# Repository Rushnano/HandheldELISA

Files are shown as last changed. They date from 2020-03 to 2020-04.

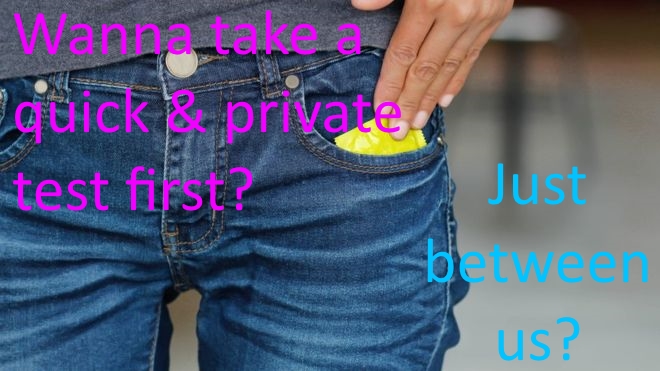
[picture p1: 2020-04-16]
images/wanna take a quick test first (annoted) 1.jpg

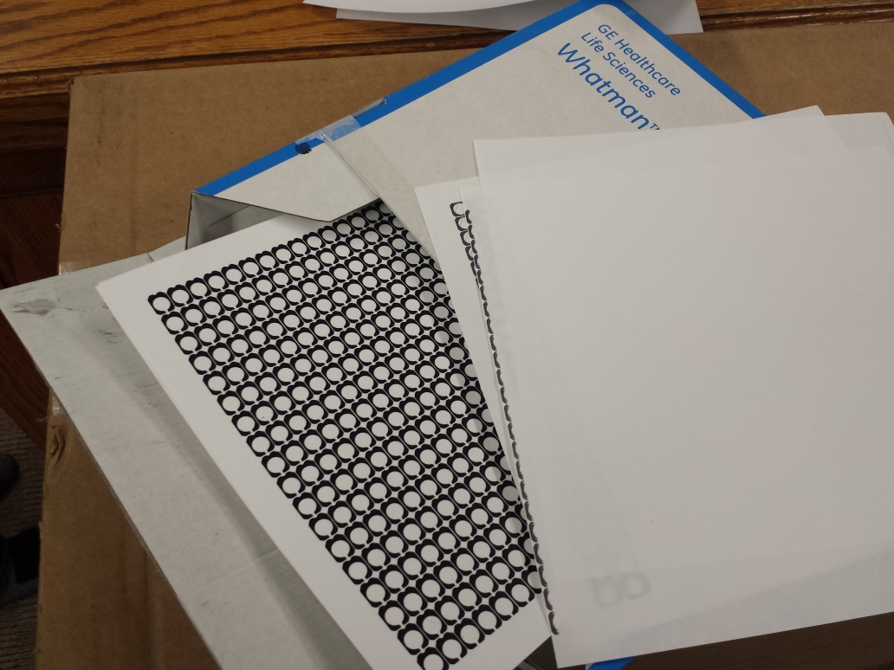
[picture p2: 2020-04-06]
screened electrode test sensors/Boundary printed 20200406.jpg

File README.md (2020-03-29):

# Handheld Point of Care ELISA
Electro Bio Chemical Potentiostat Testing Device for ELISA Test Cards
# 
  We are seeking contributors for creation of diversified testing device allowing consumable test cards capable of ELISA tests.

  The test cards may include protiens, enzymes, antibodies that allow capillary mixing and filtration with analyte so as to cause    a reaction in the working sensing zone. The working zone shall have excitation, sense and reference potentiostat electrodes for electronically sensing the the analyte/antibody reactions. The test card should also include near field radio frequency indentification for serial number, card test type, and date code.
  
  Added test card connections may also be included for electrophoresis as these electrodes may be required for fluidic movement. Hopefully we can limit these extra connections to the number of 8.

  The testing devices shall have circuitry and software included to perform a range of potentiostat test methods for a set of 2 electrode circuits. One set of electrodes will be sensing the real analyte response signal and the other set of electrodes will be used for relative reactions as reference. Potentiostat functions should be able to perform high resolution high sensitivity testing using static settings like many glucose meters to more complex features like differential pulse voltammetry.

  The testing device should be capable of near field radio frequency indentification reading for serial number, card test type, and date code to be used for test configuration parameters for that particular sensor card.

  App supported host connection using bluetooth should be included for intermediary cloud data services and display.

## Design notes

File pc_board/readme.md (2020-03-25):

#PC Board design notes

For now we will be using Altium for the source file application.

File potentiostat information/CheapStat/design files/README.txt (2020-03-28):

from: https://web.chem.ucsb.edu/~kwp/cheapstat/

schematic/ contains the EagleCAD files for schematic and board layout, parts list, and Gerber files for PCB manufacturing.

gui/ contains the Java program for receiving results from the CheapStat device via USB.  Source code is located inside .jar file.

mcu/ contains the firmware for the MCU as well as the source files.  AVRstudio 4 and WinAVR are required for compiling source code, and well as AVRISP mkII or equivalent programmer for programming the MCU.

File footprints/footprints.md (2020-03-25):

This is where the pc board part footprints will be located.

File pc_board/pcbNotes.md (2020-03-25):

PC Board design notes

For now we will be using Altium for the source file application however gerbers, pdf or image files may also be used for collaboration efforts.

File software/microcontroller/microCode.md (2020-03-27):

This is where low level firmware code will be stored primarilly in ansi C / C++. some assemble may be required. :)

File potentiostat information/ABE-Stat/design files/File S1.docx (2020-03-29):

# BE 350L

# Lab 3A Handout - Stepper Motor Control

# AEI 123 October 19, 2017

AEI 123 October 26, 2017

Report Due November 9, 2017

Revision Due November 23, 2017

In this lab exercise, you will use your Arduino skills to develop the code to control the speed of a stepper motor. Your code will issue commands to a stepper motor controller circuit “Big Stepper Driver”, via controlled pulses from a digital I/O port on the Redboard. The controller will interpret those timed pulses and sequence current to the individual motor windings accordingly. Stepper motors (a class of “brushless DC” motors that are commutated electronically by energizing individual coils in the stator, in contrast to traditional DC motors which alternate the current through brush contacts as the rotor turns) are commonly used in motion control applications because the position can be easily controlled down to the resolution of a single (or even a half) “step” without the use of sensory feedback. The motor you will use in lab (Mercury motor - spec sheet attached) is a 12V (nominal) two-phase bipolar stepper motor with 200 steps per revolution of the rotor.

You will be provided a sketch with the code for the user interface (menu) that prompts the user to select for the following options.

1. Move forward a fixed number of steps upon button press.
2. Move backward a fixed number of steps upon button press.
3. Pipette mode. Uptake media upon first button press. Dispense upon second button press.

For the first part of the lab exercise, we will create an algorithm for a controlled acceleration to the specified speed, continue at the specified speed until within 50 steps of the total steps, and then slow the speed to zero when the total number of steps have been traveled. The mechanism for turning the motor by a single step is to create a square wave pulse by turning a digital port on and then off. The motor speed will be dependent on the frequency of the pulses, so part of your algorithm will be to determine the appropriate delay between each pulse.

For example, a speed of 500 steps/sec is accomplished by pulsing the digital port HIGH for 1 ms then low for 1 ms for a total of 2 ms per step. This is the close to the maximum speed with this hardware configuration (0.7 ms delay). Similarly a speed of 1 steps/sec is accomplished by pulsing the digital port HIGH for 500 ms then low for 500 ms for a total of 1000 ms per step.

1. Open the provided stepper motor sketch “Steps test”. An external library will not be required for this application.
2. Write the code for the Steps function. The Steps function should move the motor through the specific number of steps from the revolutions setting. This function will calculate the required delay and turn the digital output port HIGH and then LOW for each step required for motion.
3. Test your code by observing the motor rotate in both directions through several angles of shaft rotation.
4. Open the provided stepper motor sketch “Lab 3 Start”. Insert the Steps function into the main loop to implement the menu functions.
  a. Move counter clockwise a fixed number of steps upon button press.
    i. Set direction.
    ii. Implement Steps function.
    iii. Reset ACTIVATE status.
  b. Move backward a fixed number of steps upon button press.
    i. Set direction.
    ii. Implement Steps function.
    iii. Reset ACTIVATE status
  c. Pipette mode (part 1). Sample upon first button press.
    i. Set direction.
    ii. Implement Steps function.
    iii. Reset ACTIVATE status
  d. Pipette mode (part 2). Dispense upon second button press.
    i. Set direction.
    ii. Implement Steps function.
    iii. Reset ACTIVATE status
5. Upload the sketch to the Redboard.
6. Power down the Redboard.
7. Connect the Redboard to the stepper motor controller.

Redboard | Controller Input
2 3 4 5 6 7 GND VCC | STEP DIR MS1 MS2 MS3 EN GND 5V

8. Make sure that the Stepper motor is connected correctly to the controller. The motor is a 12 VDC nominal bipolar stepper motor with 200 steps/ revolution. The motor leads are connected to the controller as below.

Motor | Controller Output
Red | A1
Green | A2
Yellow | B1
Blue | B2

9. Connect the drive power leads to an isolated power supply at 12 VDC (M+, GND). Do not turn on power supply.
10. Check all connections before turning devices on. Turn on Redboard first and then power supply.
11. Test your code with the 360° scale and a stop watch for forward and backward movement. Also make sure all menu functions work.

Figure 1. Sample square wave signal to control the speed of a stepper motor with the “Big Easy Driver” controller.
BE 350L

Lab 3B Handout – Automated Pippetor

For this lab you will be testing the ability of an automated pipetter to dispense liquid in both accurate and repeatable volumes. You will use the pipette driver program to run your motor controller subprogram.

1. The dispensing cycle is described in the table below. As before, the system should wait for your manual confirmation before taking a sample and dispensing a sample.

Action | Algorithm

Manual Confirmation
Take Sample | 1. Raise plunger from initial position to some top position.

Manual Confirmation
Dispense Sample | 2. Lower plunger from top position to initial position
| 3. Lower plunger from initial position to purge position.
| 4. Raise plunger from purge position to initial position.

1. Develop an experimental procedure to adequately test the ability of the pipette apparatus to dispense water. Use your experience from previous lab exercises to generate a series of tests where the travel of the plunger is compared to the volume of water dispensed and calibrate the device. Evaluate the calibration by performing additional tests while controlling the motor to dispense calibrated volumes rather than displacement settings.
2. Ensure the data set is adequate in both range and repetition to analyze the accuracy and repeatability of the pipette.
3. You will be able to measure the mass of water dispensed with an analytical balance.
4. **Prevent the motor from driving the plunger too deep and hitting the bottom of the syringe tube.

BE 350L, Fall 2017, Lab 3 Handout 1

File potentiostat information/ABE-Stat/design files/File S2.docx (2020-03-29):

BE 350L
Final Design Project
Report Due December 7, 2017

Design of thermal cycling unit for DNA amplification through polymerase chain reaction (PCR).

This lab exercise will involve the design of hardware and software components of a temperature control system. The intended application is a thermal cycler to enable the different steps required for polymerase chain reaction (PCR) amplification step. In PCR, double stranded DNA is “melted” apart at high temperature, then annealed to single stranded “primer” DNA at a lower temperature, that initiates extension of complementary sequence onto the original template DNA at an intermediate temperature. Copies of the original template DNA are then made for each thermal cycle. We will focus on temperature control for one of these steps, the actual the amplification process which can be accomplished at ~50 °C.

Thermocouples/Peltier Cooling Effect

Thermocyclers typically use Peltier cooling units to control the DNA sample temperature. The scientific principle behind the Peltier cooling technology is similar to that of a thermocouple. In a Peltier cooler, an electrical potential is applied across the junctions of two dissimilar metals, resulting in transfer of thermal energy from one junction to the other (i.e. one junction is heated while the other is cooled). Changing the polarity will reverse the direction of heat transfer, allowing one junction to be alternatively heated or cooled. In a typical Peltier unit, there are many small junction points and this arrangement is called a thermopile. Some complicated temperature measurement devices such as calorimeters also use thermopiles as a complex network of thermocouples to measure temperature around a sample in all three dimensions.

Peltier coolers are solid-state devices without any moving parts. The advantages include size, material cost, ability to cool below ambient temperatures, reliability, and low maintenance requirements. The disadvantage is that the cooling is not energy efficient and that heat from the hot side of the cooler must be constantly dissipated during operation. One of the main things to remember about a Peltier unit is that voltage only corresponds to a thermal energy difference between the two sides rather than a desired temperature at a particular side. Therefore if cooling is desired, then heat must be dissipated from the hot side so that the specified cold temperature is maintained. Alternatively, if heating is desired, heat must be directed to the cold side so that the specified hot temperature is maintained. While the rate of thermal energy transfer is proportional to the applied current between the junctions, application of current also results in ohmic heating throughout the device which is proportional to the square of current. Therefore there is a physical limit to how much a junction can be cooled even if the “hot” junction is maintained at ambient temperature.

State 1

Temperatures of each side are the same T1 = T2.

TC

State 3

Side 1 cooled. Heat pumped from cold side to hot side. Lowest TC achieved by ΔT = TH - TC. Must remove heat from hot side keep TH from rising too high.

TH

TH

State 2

Side 1 Heated. Heat pumped from cold side to hot side. Highest TH achieved by ΔT = TH - TC. Must draw in heat to cold side keep TC from falling too low.

TC

T1

T2

Figure 1. Illustration of temperature control for cooling and heating applications with a Peltier cooler.

The rate at which the Peltier unit can pump heat from its cold side to hot side is a function of the temperature difference between the two sides. The measured performance as supplied by the manufacturer Cui Inc. is given in Figure 2. At a given voltage applied to the terminals, e.g. 4 V, the top plot can be used to determine current draw. That current draw can then be located on the bottom plot to determine a relationship between the heat pumped and the temperature difference between the two sides.

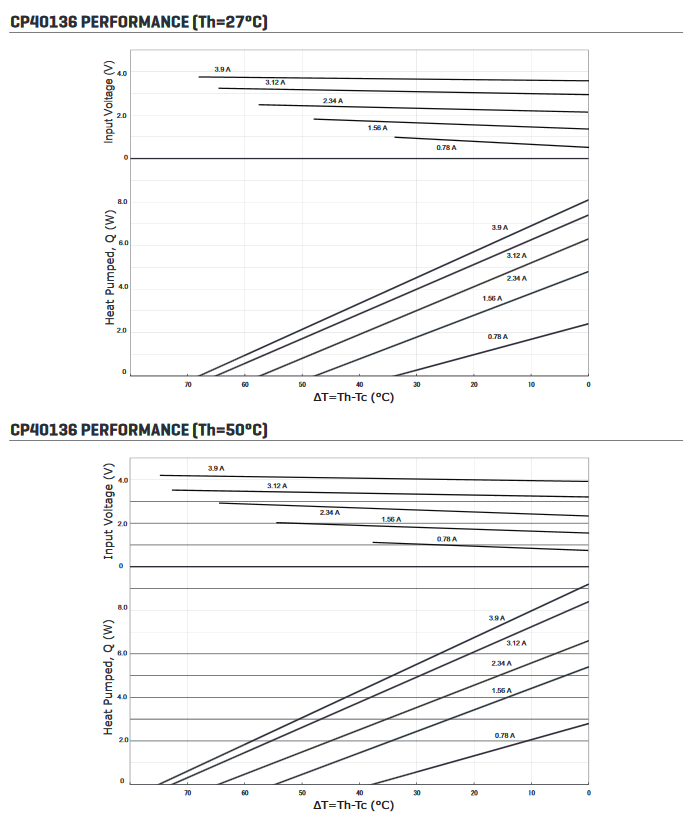
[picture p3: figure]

Figure 2. Performance of the CP40236 Peltier cooler at hot side temperatures of 27 and 50 °C.

Methods

The performance criteria that you will be evaluating are 1) rate of temperature change within the sample as well as 2) a uniform temperature distribution within the sample. You must design the heat sink such that you obtain a reasonable temperature ramping. You must also consider how to achieve a uniform temperature distribution within the sample.

Over the course of this multi-part laboratory exercise, there are several exercises to be completed. Remember, these are methods and the actual experimental objective(s) should be written in your own words.

- First generate an analytical model on this thermocycler system. These first calculations will serve as the basis for future decisions with the heat sink design and analysis of the results. Run models for both heating and cooling processes by changing the initial temperatures.
- Conduct simulations within Solidworks to further study not only the temperature ramping, but also the temperature distribution within the sample. Again, run models for both heating and cooling processes by changing the initial temperatures. Submit a final heat sink design for fabrication by the instructor.
- Design and conduct experiments on the thermocycler using the heat sink that the group has designed.
- Analysis will be made on all of the above results and design changes should be proposed if necessary.

Analytical Model

During the first period you will be performing basic energy balance analyses to characterize the temperature change over time for a sample block and heat sink fabricated from 6061 aluminum. The dimensions of the sample block and initial heat sink are 1” x 1” x 0.75” and 3” x 1” x 0.5” respectively. You may assume that heat conduction within the aluminum occurs much faster than all other processes such that the temperatures are uniform within the sample block and heat sink separately. Initially you may choose a constant power transfer between the two blocks, however you should refine your model to include a formula for the power transfer derived from the manufacturer’s data table for your Peltier unit. Assume that the sample block and heat sink exchange heat with the ambient air, but do not exchange heat with each other. This model will help determine the power transfer value to use in the computer simulation. You will need to look up an appropriate convective heat transfer coefficient for air. You may (should) use Matlab to execute the solution of this non homogeneous system and to plot your results.

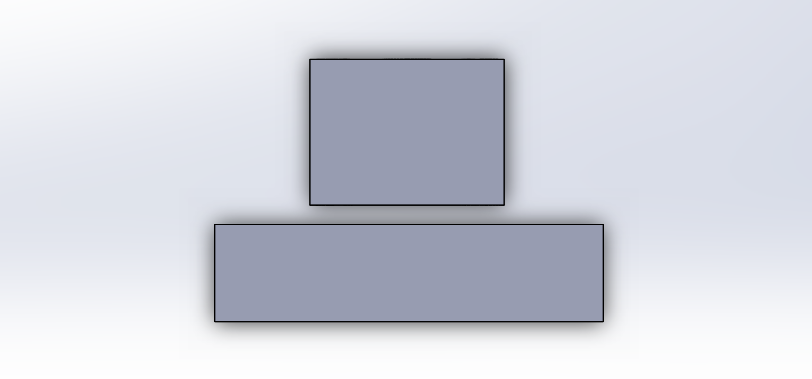
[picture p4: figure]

Figure 3. Layout of the sample block (above) and heat sink (below) in the thermocycler. Peltier unit not pictured.

Heat Sink Design

Alter the design of the heat sink either by changing the size or by adding fins or other geometries to enhance convective heat exchange. Design the heat sink to maintain temperatures that are desirable for the heating and cooling cycles of the thermocycler. Strike a balance between increasing the surface area while preserving the mass of the heat sink. The minimum and maximum dimensions for the heat sink are 1” x 1” x 0.5” and 1” x 3” x 0.5” respectively. Each participant should design at least one of their own heat sinks.

Solidworks Simulation

During the second period, you will be using Solidworks to create 3D drawings for the heat sink, sample block, and DNA (water) sample separately. Complete these drawing using the provided specifications. Solidworks will then be used to run multiple thermal simulations. Just as with your initial analyses of this system, you will need to define any process that will affect the energy stored in each component as well as the initial conditions, material properties, and boundaries. Solidworks will divide the parts into a finite number of elements and calculate the heat transferred between adjacent elements. This technique is called finite element analysis.

The simulation for the sample block and heat sink will be conducted separately. For the sample block simulation, insert the sample block and sample parts into an assembly and add the appropriate mating constraints to align the parts. This can be reviewed together in class.

1. Open a New Study under the Study Advisor drop down menu in the Simulation tab. Select a Thermal study for the current simulation. Take note of the parameters of the thermal study as seen under the Feature Manager window on the left.
- Parts – Select material composition of each part.
- Connections – Choose whether contacts between components will be insulated.
- Thermal loads – Processes that affect the energy stored in each component
  - Temperature – Can set an initial temperature of component or define a constant temperature to a surface.
  - Convection – Define a convective heat transfer process.
  - Heat Flux – Define a constant heat transfer flux process (power/area).
  - Heat Power – Define a constant heat transfer process.
  - Radiation – Define a radiative heat transfer process.
- Mesh – Create parameters to generate the finite element mesh.
2. Right click on the name of the study and choose to edit Properties. Change the study from a steady-state to a transient analysis and set the time range and time step.
3. Add/Edit the material for each part and select 6061-T6 aluminum for the sample block and heat sink. Select water for the sample.
4. Create an Insulated contact set.
5. Add a Temperature thermal load. Select Initial Temperature and select both components. Set the temperature to 25 °C. This thermal load must be the first one added.
6. Add a Convection thermal load. Look up an appropriate convective heat transfer coefficient and select an ambient temperature of 25 °C.
7. Add a Heat Power thermal load. Select the top face of the heat sink and define the heat power.
8. Add a Heat Power thermal load. Select the bottom face of the sample block and define the heat power.
9. Create a Mesh and then Run the simulation.
10. You can save a copy of the resulting surface plot as a jpeg file.
11. Create a Section Clipping to display the internal temperature uniformity of a slice.
12. Under Plot Tools, use the Probe option to select points along the cross-sectional slice and choose a Response plot to display how the temperature changes at specific points over time.

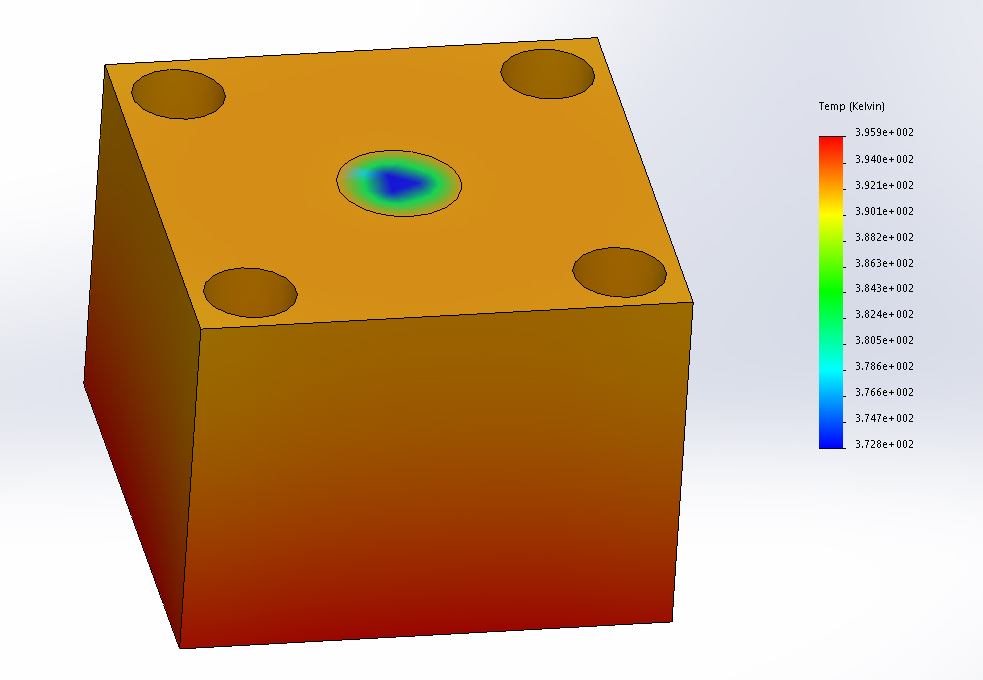
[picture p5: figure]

Figure 4. Color plot of the temperature distribution along the surface of an aluminum sample well block with heating along the bottom surface. Note that due to the relatively high thermal conductivity of aluminum the temperature distribution is mostly uniform.

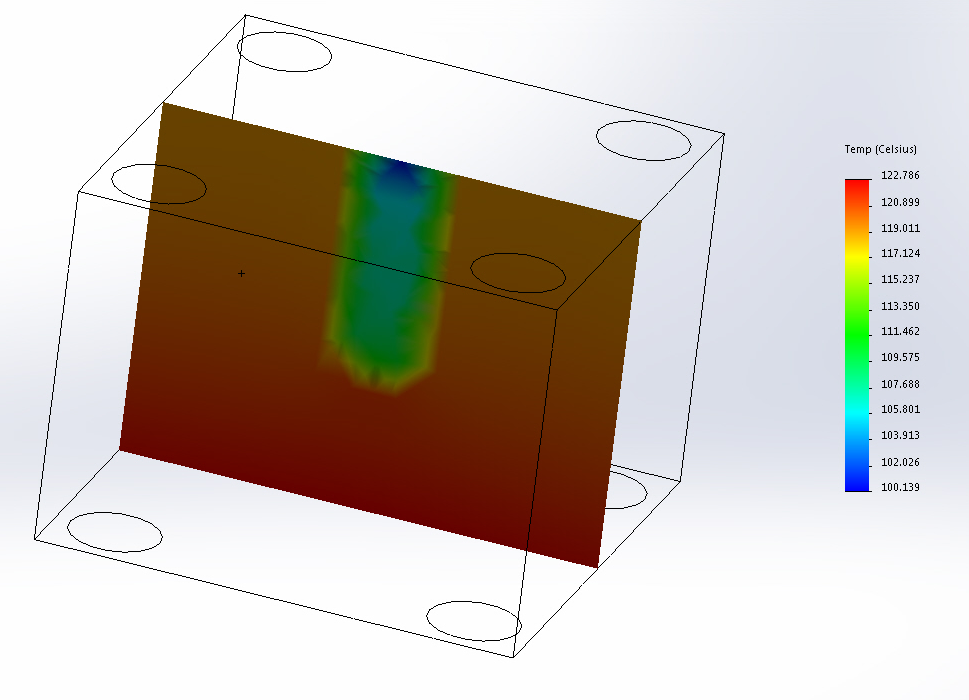
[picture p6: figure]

Figure 5. Temperature distribution of a cross section through the center of the middle reaction well. Notice that the bottom and sides of the well are hotter than along the top and center.

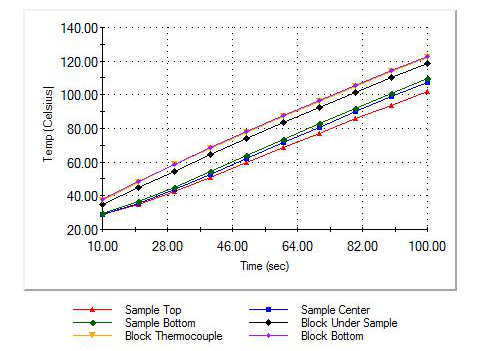
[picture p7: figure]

Figure 6. Transient temperatures simulated at multiple points along the sample well axis. Note that the bottom of the well responds faster and gets hotter than the top.

13. Right click on the thermal study tab and duplicate the study. You may choose to name the new study “cooling” or something similar. Modify the study to simulate cooling of the sample block and water sample assembly. Change the initial temperature to 50 °C and the reverse the direction of the heat power. Run the simulation again and save any desired results in tables or graphs.
14. Run cooling and heating simulations for the heat sink which you can conduct right from the part file. You do not need to create an assembly. Save any desired results. Each group member can run simulations with the heat sink they designed.
15. At this stage, you can also redesign your heat sink within the model window. Modify the heat sink by changing the length or cutting away material. Before you run new cooling and heating simulations, apply a mesh again. This will update the geometries in the thermal studies and you should not need to redefine all the parameters again.

Experimental Procedure

16. Design and conduct experiments to validate your simulation results. Make notes of any assumptions made during the simulation and design your experiment to be as consistent with most of these assumptions as possible. Each test that you run, may help you to not only assess the design but also refine your simulation settings, for example the convective heat transfer coefficient value or power addition/removal.

Minimum Report Requirements

17. The report should have the usual required sections.
18. Recall the two design criteria. There should be a timely temperature ramping to the desired temperature and the temperature of the sample should be relatively uniform.
19. There will be a lot of information that can go in the methods section and you will need to organize it and present it well. From the analytical model, you will get an idea for what the heat transfer power range of the Peltier unit will be as well as model for the temperature of the components as a function of time. This information along with your research into an appropriate convective heat transfer coefficient value will likely have a significant impact on the simulation results. How you determined these parameters should be explained in this section.
20. There can also be an abundance of graphs and results for your results and discussion section, so again organize and present the material well. Simulation and experimental results should be discussed here individually as especially as relating to the objectives as well as compared. After analyzing both results, you modified the simulation, discuss that here as well.
21. In the conclusion, briefly summarize the results in the context of the objectives. Also suggest design changes or the next step(s) in the design or development process.

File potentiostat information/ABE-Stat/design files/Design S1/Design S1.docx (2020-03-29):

Supplemental Material, Design S1 (Coffee Cherry Color Sorter)

Schematic

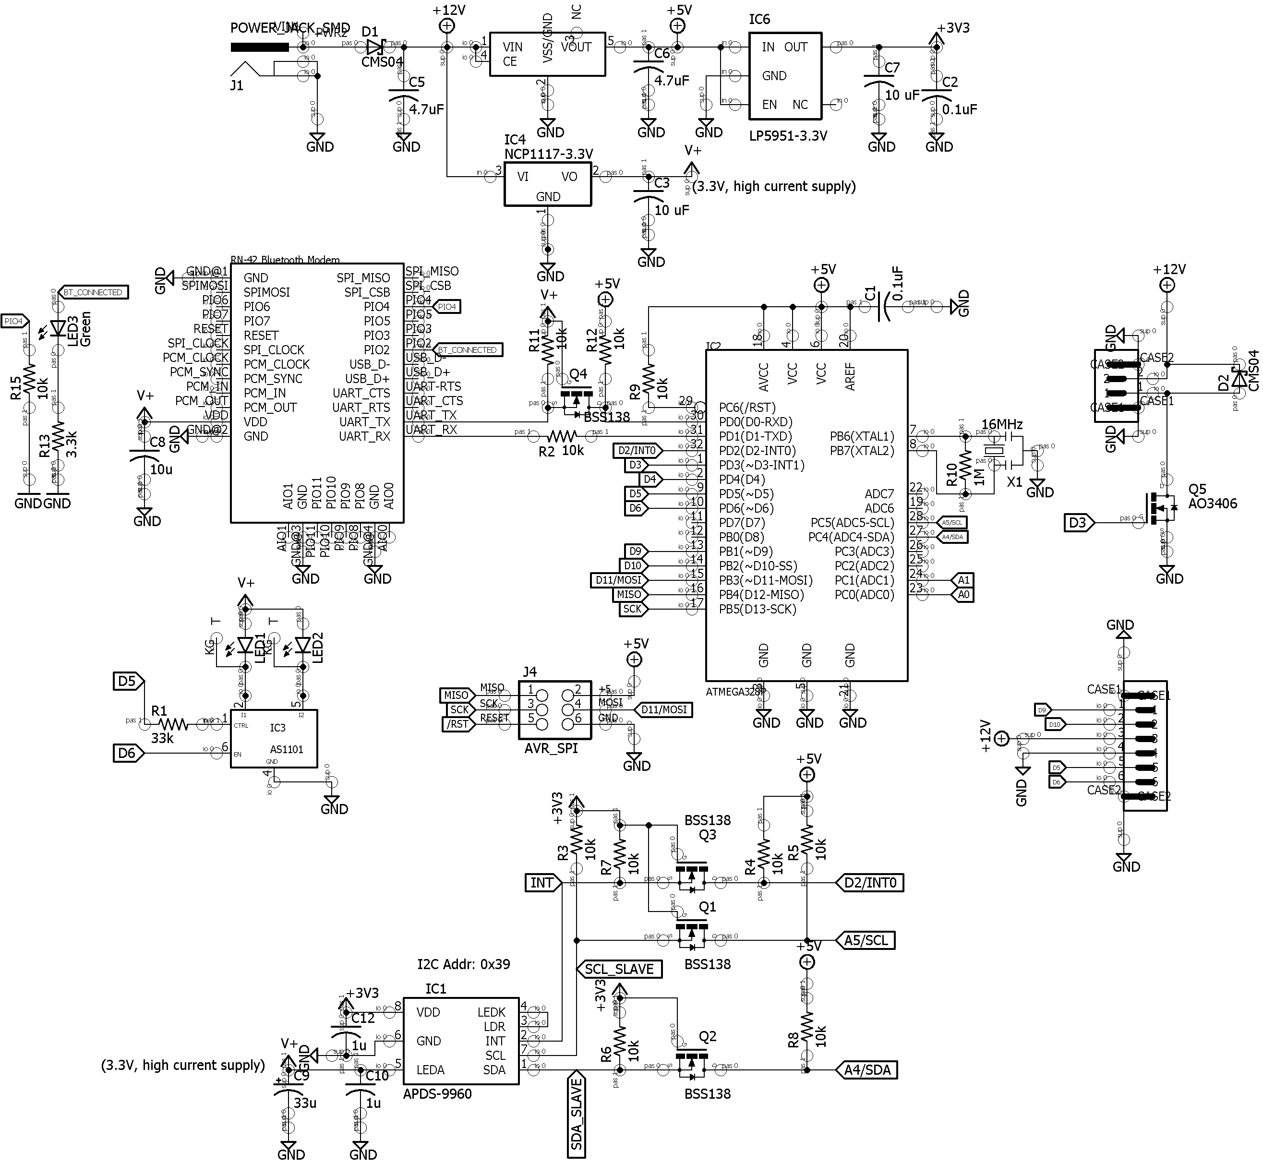
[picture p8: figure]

Layout

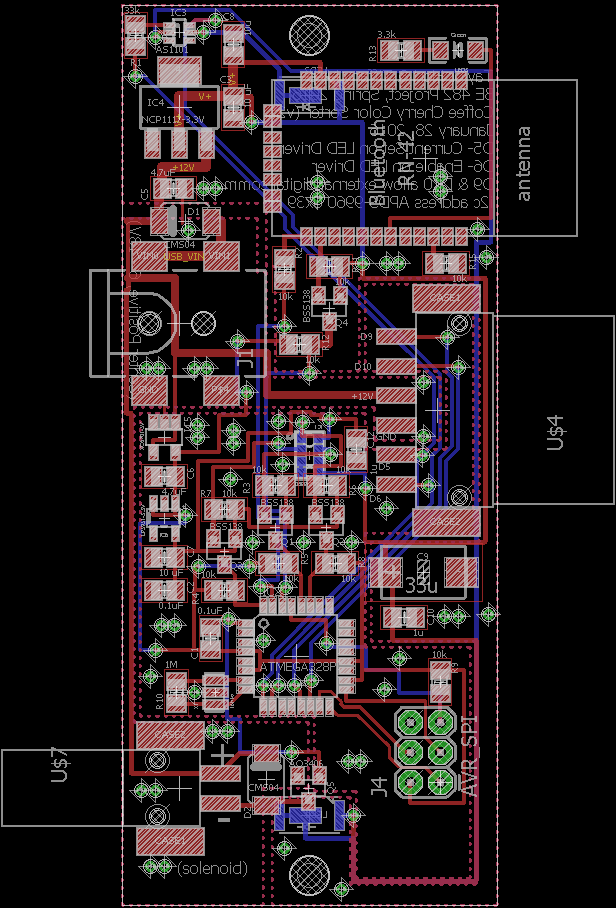
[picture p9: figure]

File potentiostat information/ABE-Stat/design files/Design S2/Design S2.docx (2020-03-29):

Supplemental Material, Design S2 (ABE-Stat 1_0_01 Wireless Potentiostat Prototype)

Schematic

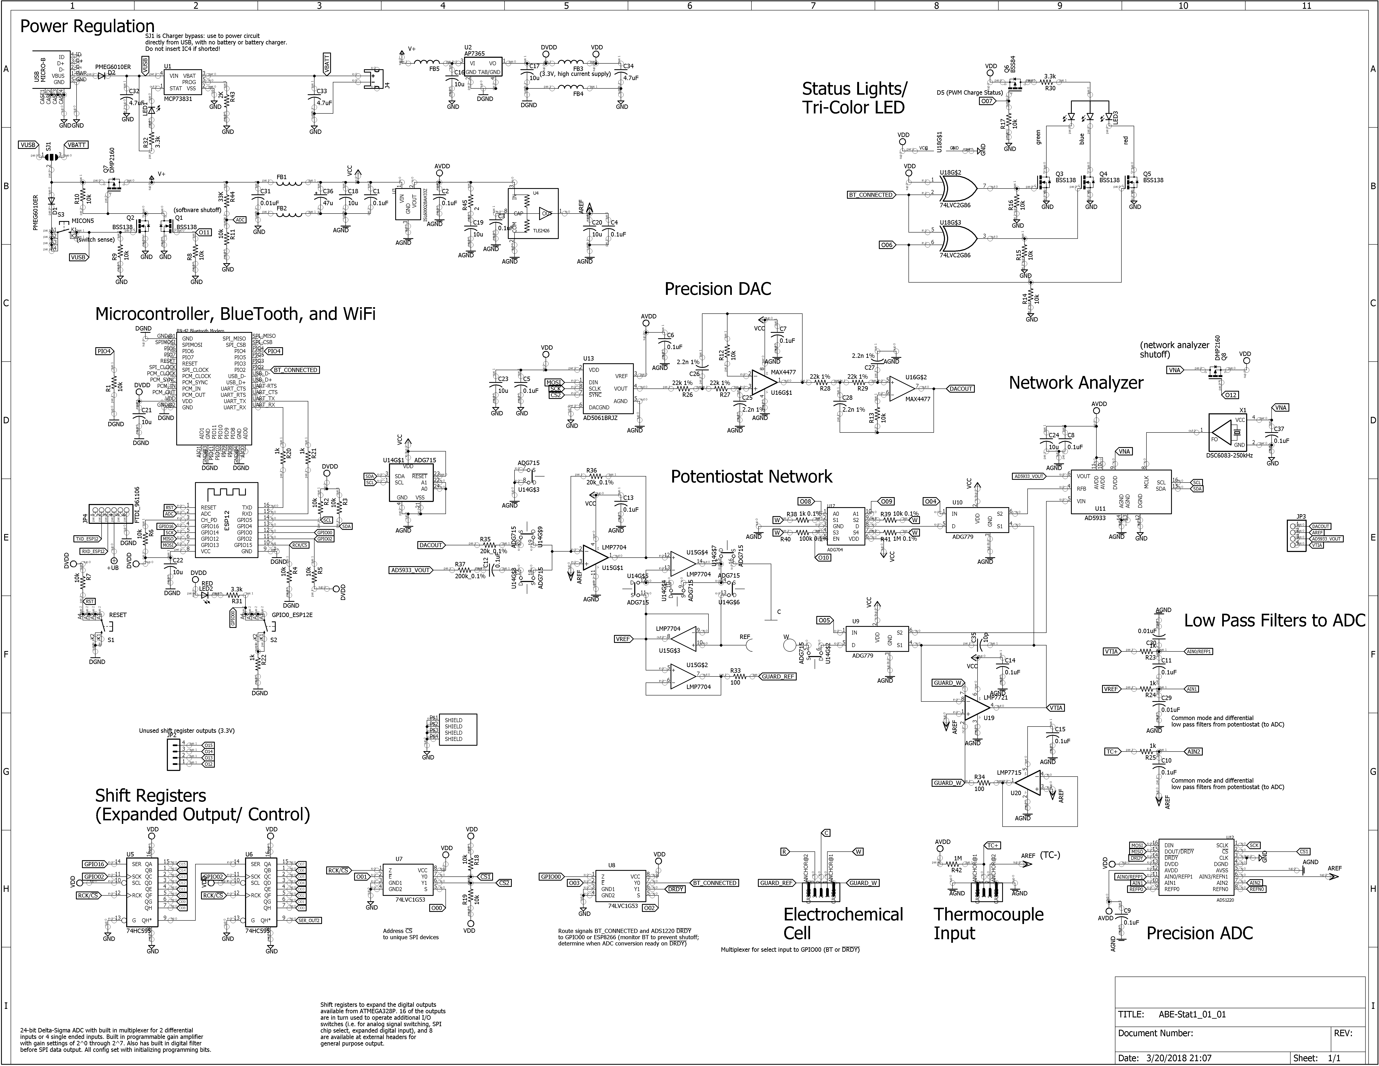
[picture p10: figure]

Layout

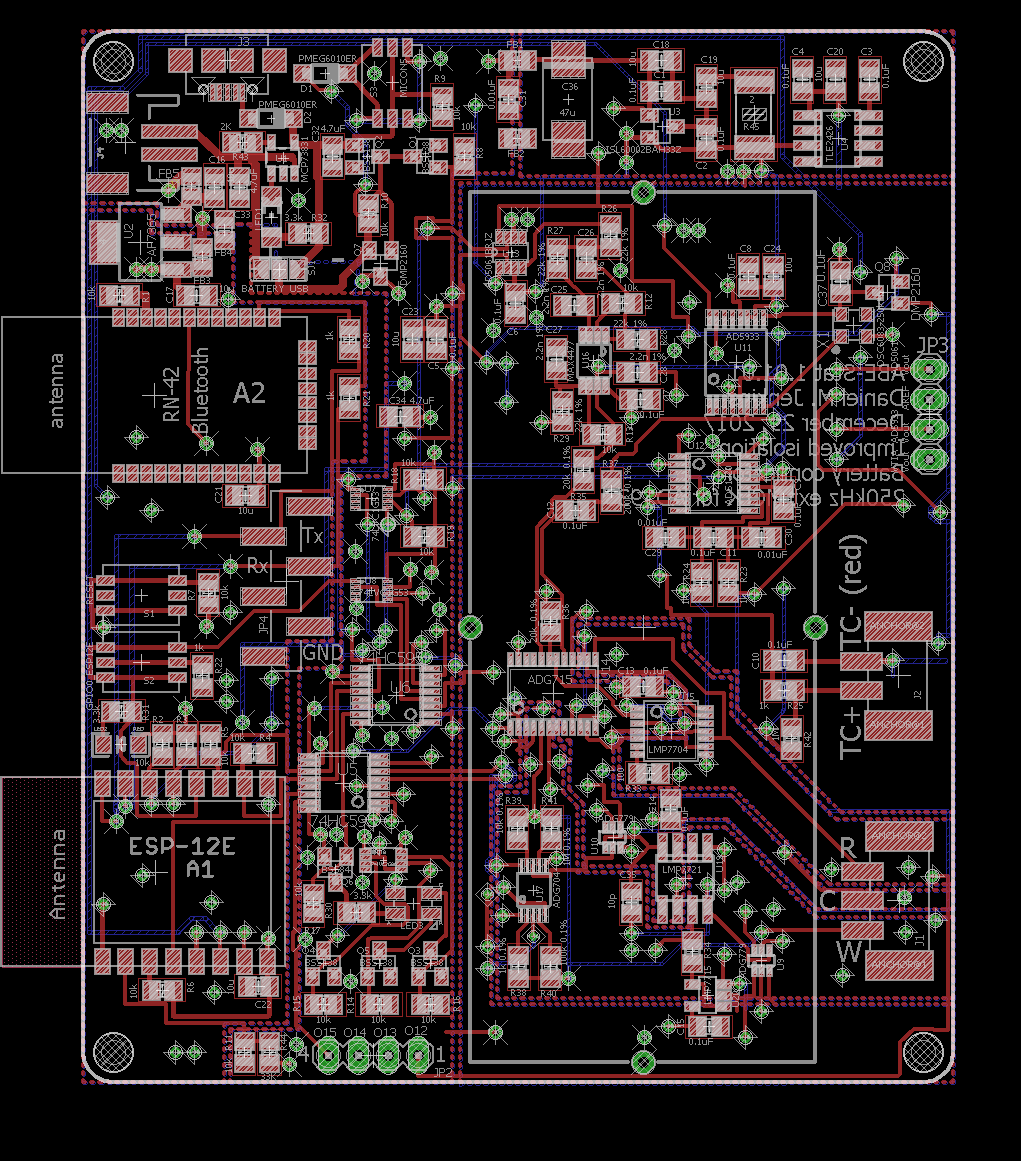
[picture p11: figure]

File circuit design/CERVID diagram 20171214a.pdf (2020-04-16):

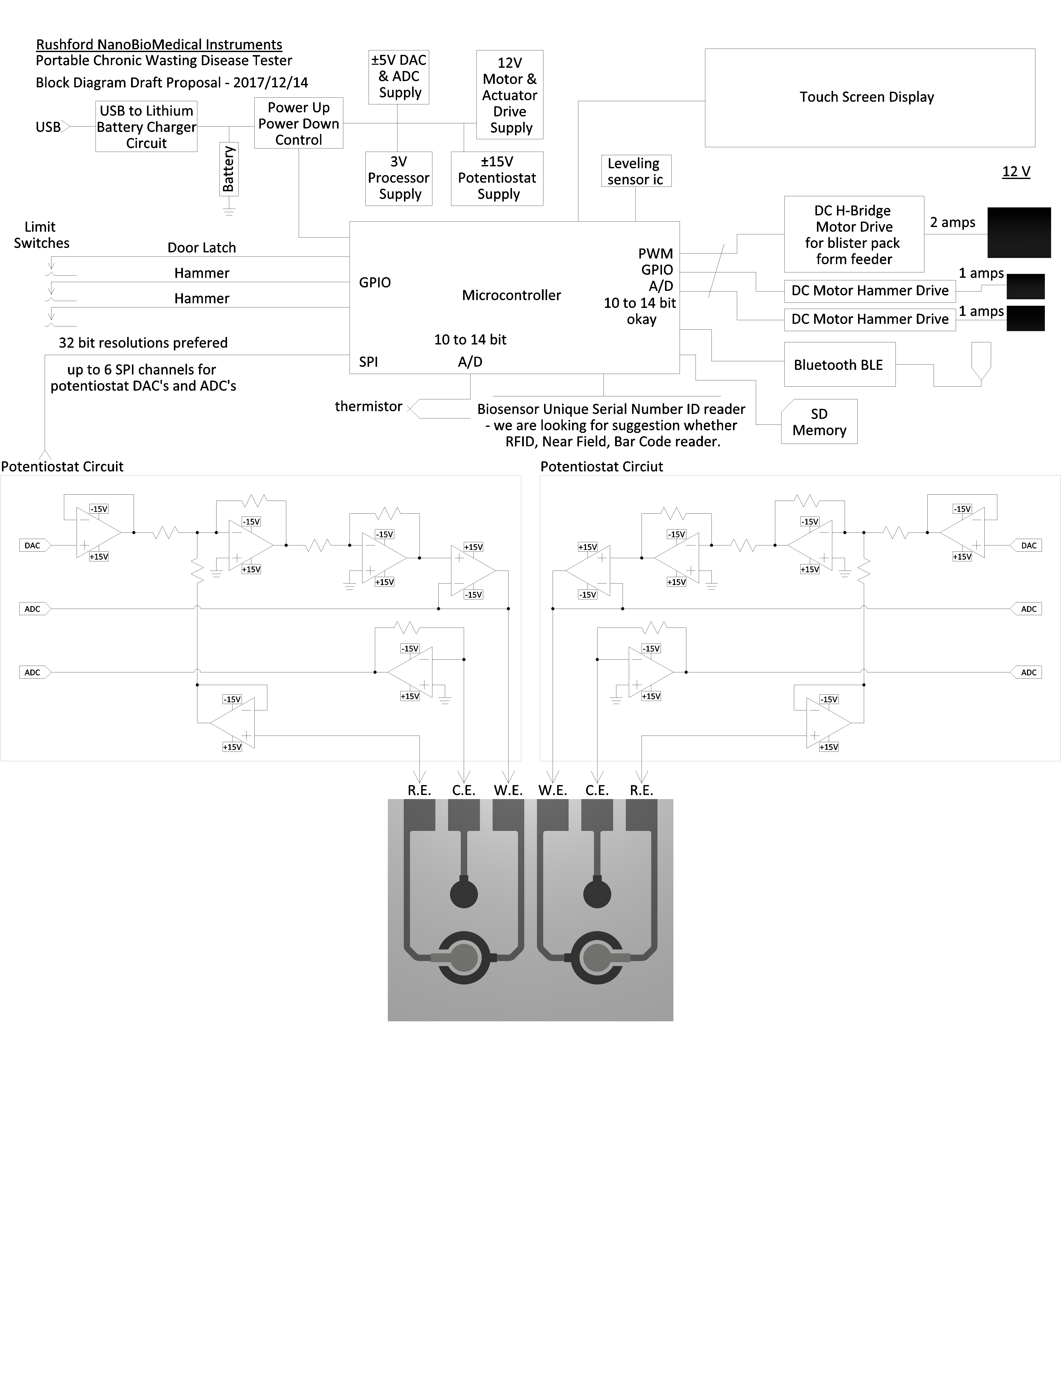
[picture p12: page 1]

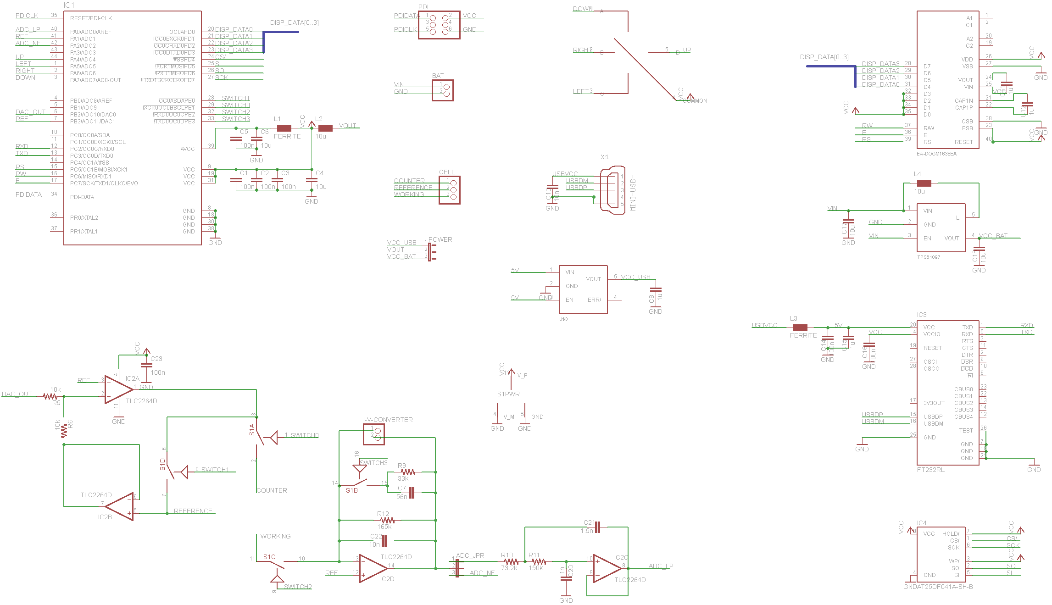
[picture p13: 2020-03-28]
potentiostat information/CheapStat/design files/schematic/schematic.png

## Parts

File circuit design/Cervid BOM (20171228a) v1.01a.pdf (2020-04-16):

Cervid BOM v1.01a.xls

Line Item | Quantity | Reference Designation | Value | Description | Manufacturer | Part Number
1 | 1 | U1 | | Microcontroller | Texas Instruments | MSP430F5529IPN
2 | 1 | U2 | | Bluetooth LE Controller | Texas Instruments | CC2640R2FRHBR
3 | 1 | U3 | | 32 Bit Digital to Analog Converter 2 Channel | Asahi Kasei Microdevices | AK4493EQ
4 | 1 | U4 | | 32 Bit Analog to Digital Converter 4 Channel | Asahi Kasei Microdevices | AK5534VN
5 | 1 | U5 | 8-38V 2.8A | Motor Driver - Form Feed | Texas Instruments | DRV8801RTYR
6 | 1 | U6 | 4-18V 1.4A | Dual Solenoid Drivers - Bladder Hammers | Texas Instruments | DRV8846RGER
8 | 1 | U7 | 3.3V | Switching Power Supply 3.3V | Texas Instruments | TPS61221DCKR
9 | 1 | U8 | 5V | Switching Power Supply 5V | Texas Instruments | TPS61222DCKR
10 | 1 | U9 | 12V, 2A | Switching Power Supply 12V | Linear Technology | LT1109ACS8-12#PBF
11 | 1 | U10 | ±15V | Switching Power Supply ±15V | Texas Instruments | TPS65130RGER
12 | 1 | U11 | | Angle Sensor | NXP | KMZ49,118
13 | 7 | U12, U13, U14, U15, U17, U18, U19 | | High Impedence, High Slew Rate, Low Noise Op Amps | Texas Instruments | OPA637AU
14 | 1 | Y1 | 32.768kHz | Crystal | Seiko | SSP-T7-F
15 | 1 | H1 | | Secure Digital Memory Socket | Amphenol | 101-00405-75
16 | 1 | H2 | | Mini USB Connector | Amphenol | 10118194-0001LF
17 | 1 | H3 | | Litium Battery Connector | JST | S2B-PH-K-S(LF)(SN)
18 | 1 | H4 | | Display Connector | TE Connectivity | 84952-6
19 | 1 | DISPLAY | | Touch Screen Display | Displaytech | DT035BTFT-PTS1

Resistors
Capacitors
Inductors
Connectors
Limit Switches

NFC/RFID Biosensor ID

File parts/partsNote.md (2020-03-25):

Evaluated and implimented technical part documents will be located here.

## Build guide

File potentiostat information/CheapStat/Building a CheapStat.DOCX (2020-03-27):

General Instructions for building a CheapStat portable potentiostat.

1// Circuit Board

Send the Gerber files to a printed circuit board manufacturer, and order one or more of the CheapStat printed circuit boards. The gerber files are available as supporting information, and updated versions may be found on our website.

2// Parts List

Order the parts from a vendor such as digikey or Mouser electronics. See table S1 for a full list of parts. Some of these components may be substituted or omitted. For instance, this device can function with a wide variety of different flash chips.

3// Soldering

Solder all of the components onto the printed circuit board as indicated in figure S1. You can zoom in on this schematic, or look at the gerber files and the photos below (S2 and S3) for further clarification. If you do not have the appropraite soldering equipment, contract circuit assembly firms such as Sandberg Industries (Santa Ana, California) can do it for you for a reasonable fee. Be sure to wear an antistatic wrist strap when handling the components.

4// Mounting the board.

You will need to cut several holes in the enclosure (Fig S2 and S7) to handle the LCD display, USB port, and control switch. This can be done with a dremmel rotary tool.

5// Programming the microcontroller.

On the circuit board, there are a set of six pins that can be plugged into a microcontroller programmer. First, attach the cheapstat to a USB power source. Then, attach the microcontroller programmer. Finally, upload the firmware files to the microcontroller (available in supporting information). This process should take a few minutes. This is the final step of the assembly process.

6// Using the cheapstat

With the CheapStat plugged into the USB port of a computer, start the control software program. Use the four way switch on the CheapStat to select an experiment mode such as Square Wave Voltammetry, change the parameters, and run an experiment. Be sure that the control software is set to the correct COM port.

7// Handling Data

Data from the cheapstat can be copied directly into Microsoft Excel, Open Office, or other spreadsheet programs.

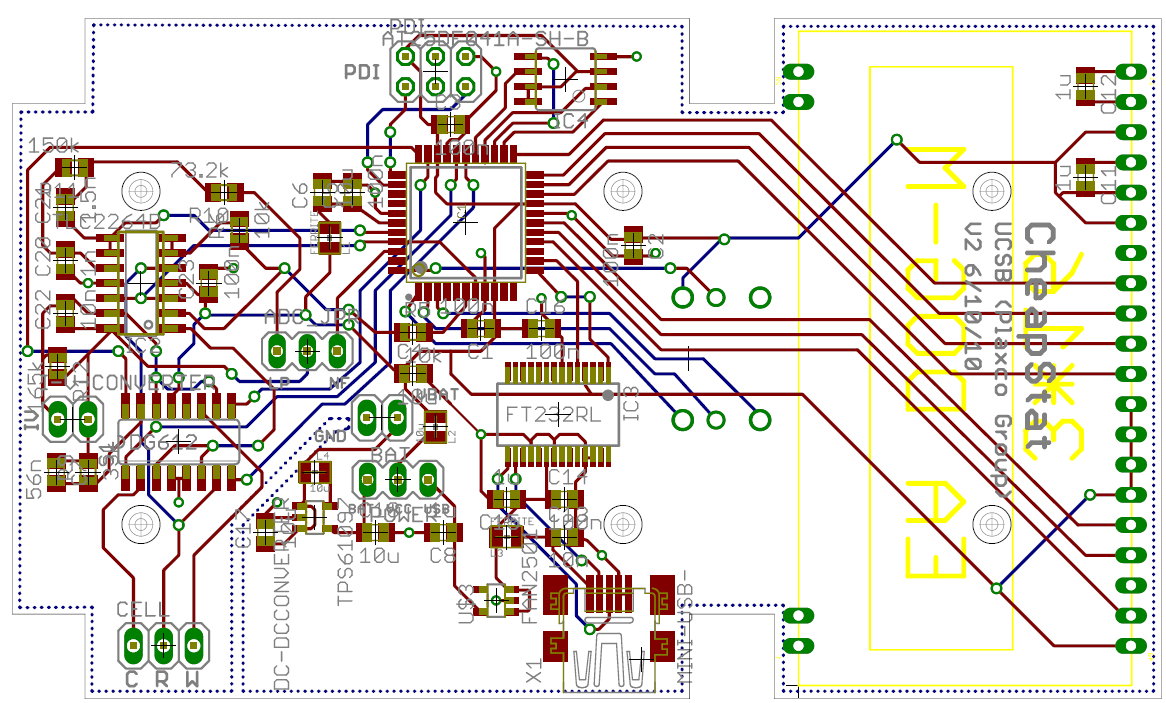
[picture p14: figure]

Figure S1 – Board layout. An Atmel XMEGA microcontroller containing a DAC and an ADC with precision sufficient for voltage waveform generation and current quantification. An RS-232 chip provides an interface between this microcontroller and a data analysis computer via a USB port. An op amp feedback system sets the voltage across the electrochemical cell and supplies the voltage needed to drive the electrochemical reaction.

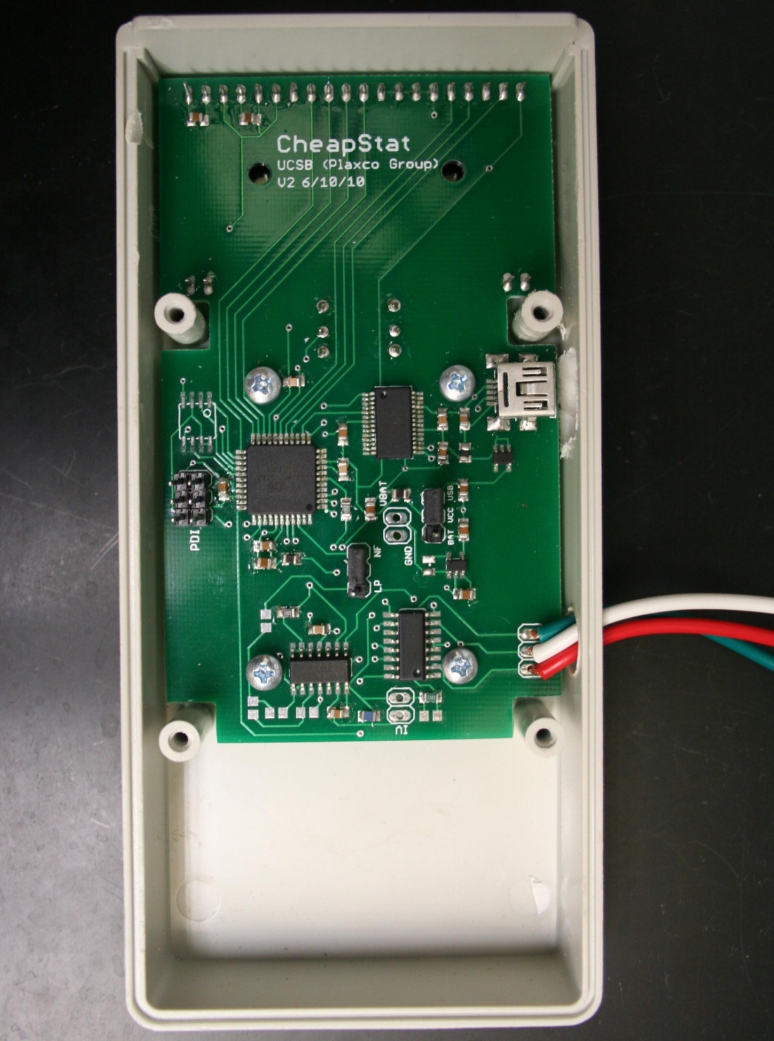
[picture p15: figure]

Figure S2 – The front side of the circuit board has a mix of surface mount and through-hole solder connections. Many of the components have a fine pitch, meaning that the electrical contacts are very close together. Nevertheless, all of the components were placed by hand and soldered without the assistance of a reflow oven.

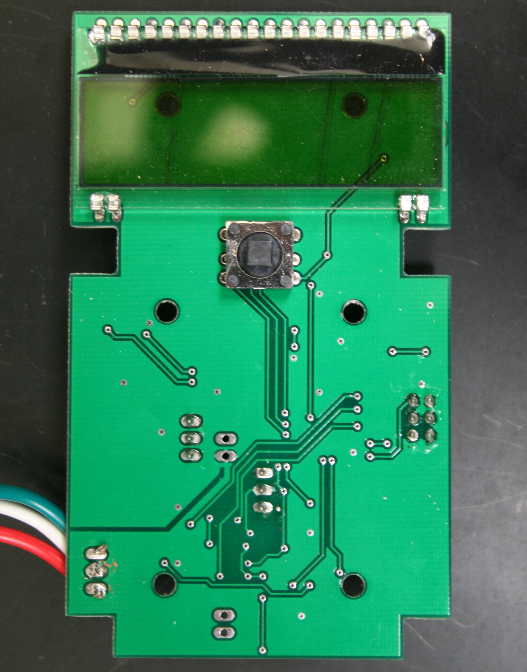
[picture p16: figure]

Figure S3 – The reverse of the circuit board supports a three-line LCD display and a joystick, which is used to select an experiment protocol, change its parameters, and initiate experiments.

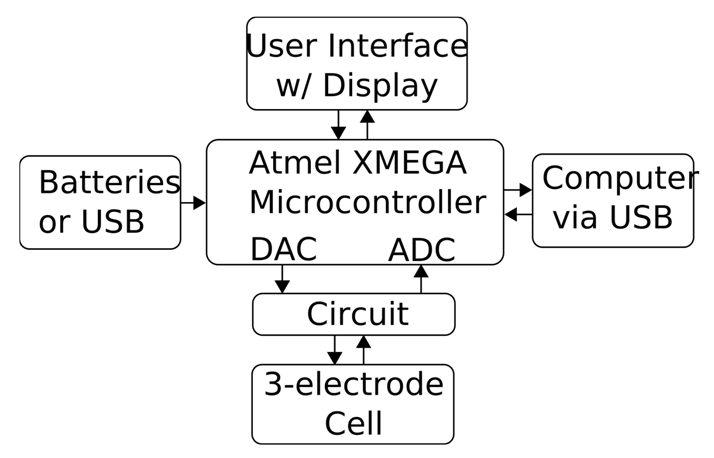
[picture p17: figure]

Figure S4 – A block diagram shows the relationship between the microcontroller and other components.


Figure S5 – A circuit schematic, detailing the connections between each of the main components. Zoom in to see the details.

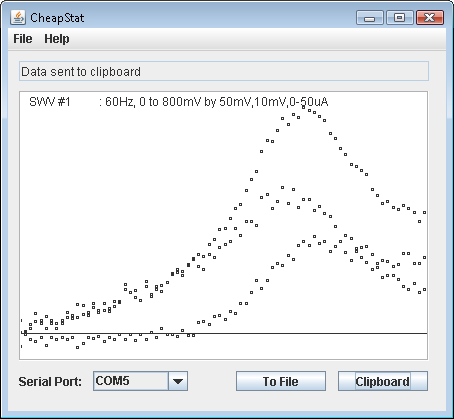
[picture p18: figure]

Figure S6 – Screen shot of the control software in action. Data can be copied to the computer clipboard with a single mouse click or saved into a new file within seconds.

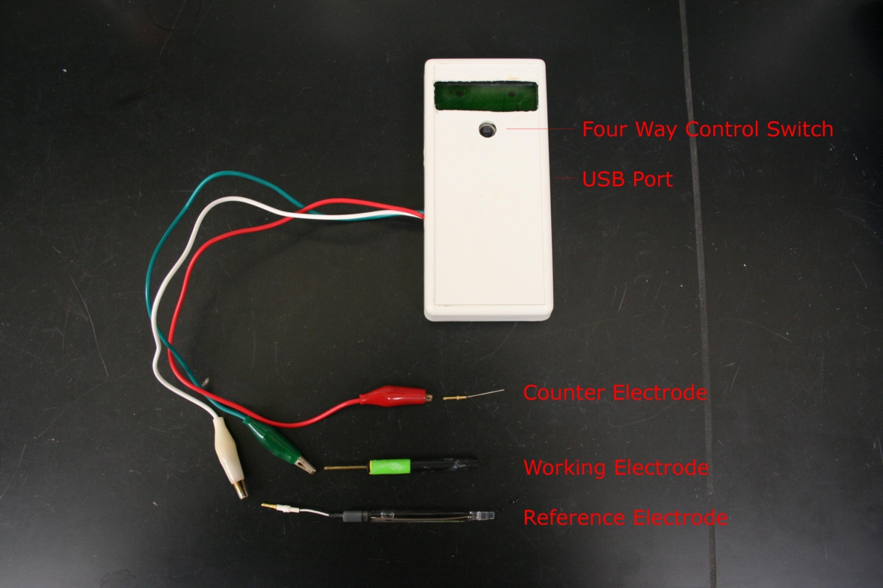
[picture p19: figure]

Figure S7 – Key features of the device. The red wire should be attached to a counter electrode. The green wire can be attached to a working electrode. The white wire can be attached to a reference. The device is controlled with a four way switch, and there is a USB port on the side, which supplies power and an interface with any netbook, laptop, or desktop computer.

Table S1 -- Cheapstat Version 2.0

Complete Parts List

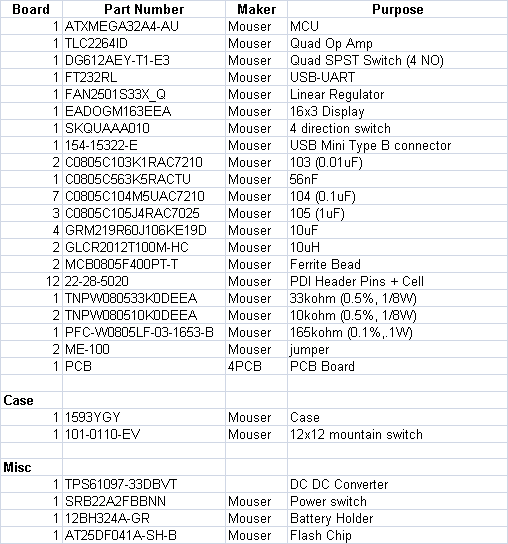
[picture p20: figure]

Key Features of the CheapStat

Square Wave Voltammetry

Alternating Current Voltammetry

Linear Sweep Voltammetry

Constant Potential Mode

Frequency Range: 1-1000Hz

Voltage Range: -990 to 990mV

Current Range: ~100nA to ~10µA

Note for Early Adopters

For information demonstrating proper use of the CheapStat, as well as updates to this design, circuit board layout, and source code, can be found on the website of Professor Kevin Plaxco, where it is available free of charge.

http://www.plaxcolab.com/cheapstat

or

http://www.chem.ucsb.edu/~kwp/cheapstat/

Feel free to email us with questions. We’re friendly!

We welcome design suggestions and code.

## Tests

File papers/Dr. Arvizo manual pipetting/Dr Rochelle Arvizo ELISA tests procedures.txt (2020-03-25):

1. Add capture antibody to the "work zone" and incubate for 25 minutes at room temperature.
2. Wash off any unincorporated anibodies with phosphate-buffered-saline (PBS) or blocking buffer using blotting paper.
3. Incubate with blocking buffer for 30 minutes at room temperature.
4. Rinse again - see step 2.
5. Add the analyte solution and incubate for 200 seconds at room temperature.
6. Wash with blocking buffer / phosphate-buffered-saline link in step 2.
7. Incubate with the signaling antibody for 200 seconds at room temperature.
8. Follow with a rinse step like step 2.
9. Run your test. :)

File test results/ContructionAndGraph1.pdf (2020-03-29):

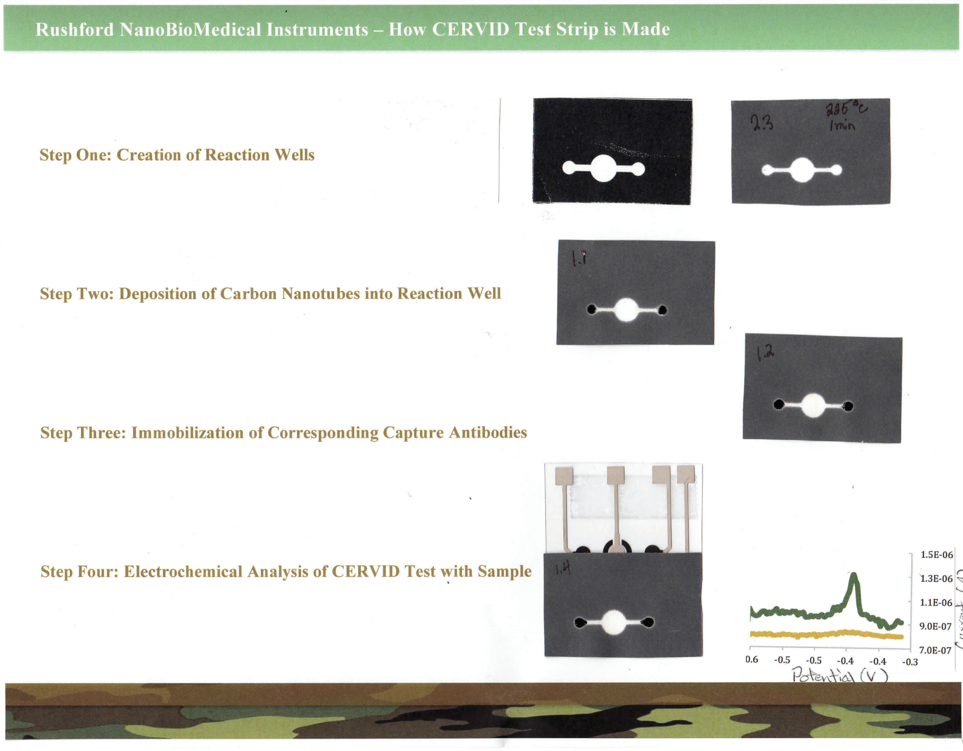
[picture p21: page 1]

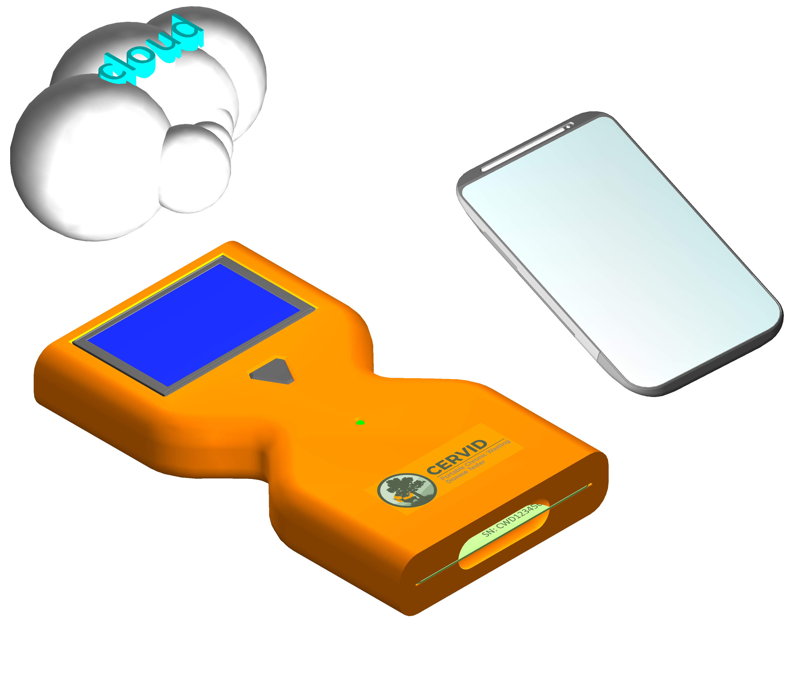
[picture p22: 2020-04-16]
animations/20180114a/CERVID Tester (3d) 20180114a-46.png

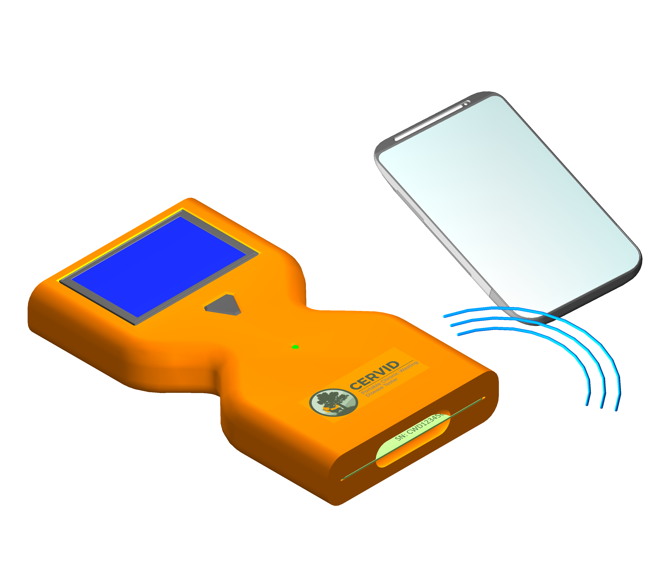
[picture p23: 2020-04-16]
animations/20180114a/CERVID Tester (3d) 20180114a-32.png

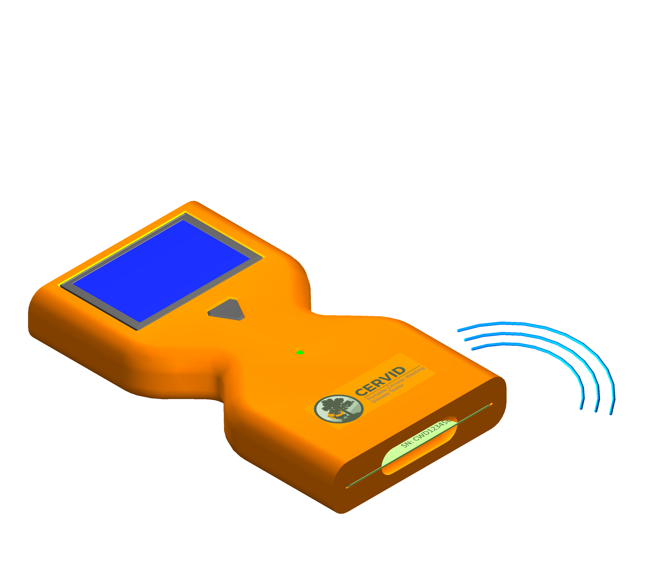
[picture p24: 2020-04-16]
animations/20180114a/CERVID Tester (3d) 20180114a-21.png

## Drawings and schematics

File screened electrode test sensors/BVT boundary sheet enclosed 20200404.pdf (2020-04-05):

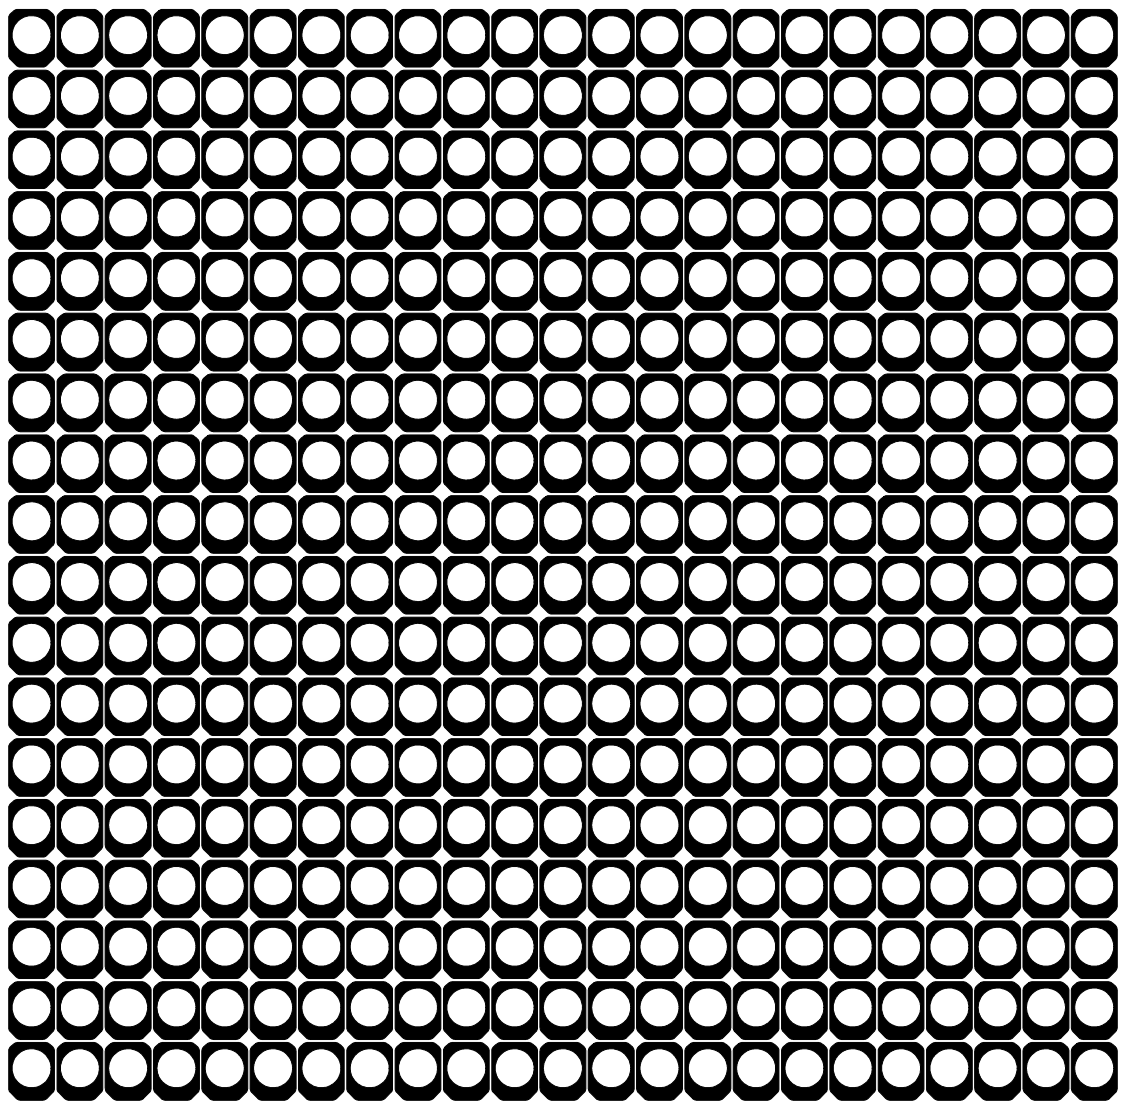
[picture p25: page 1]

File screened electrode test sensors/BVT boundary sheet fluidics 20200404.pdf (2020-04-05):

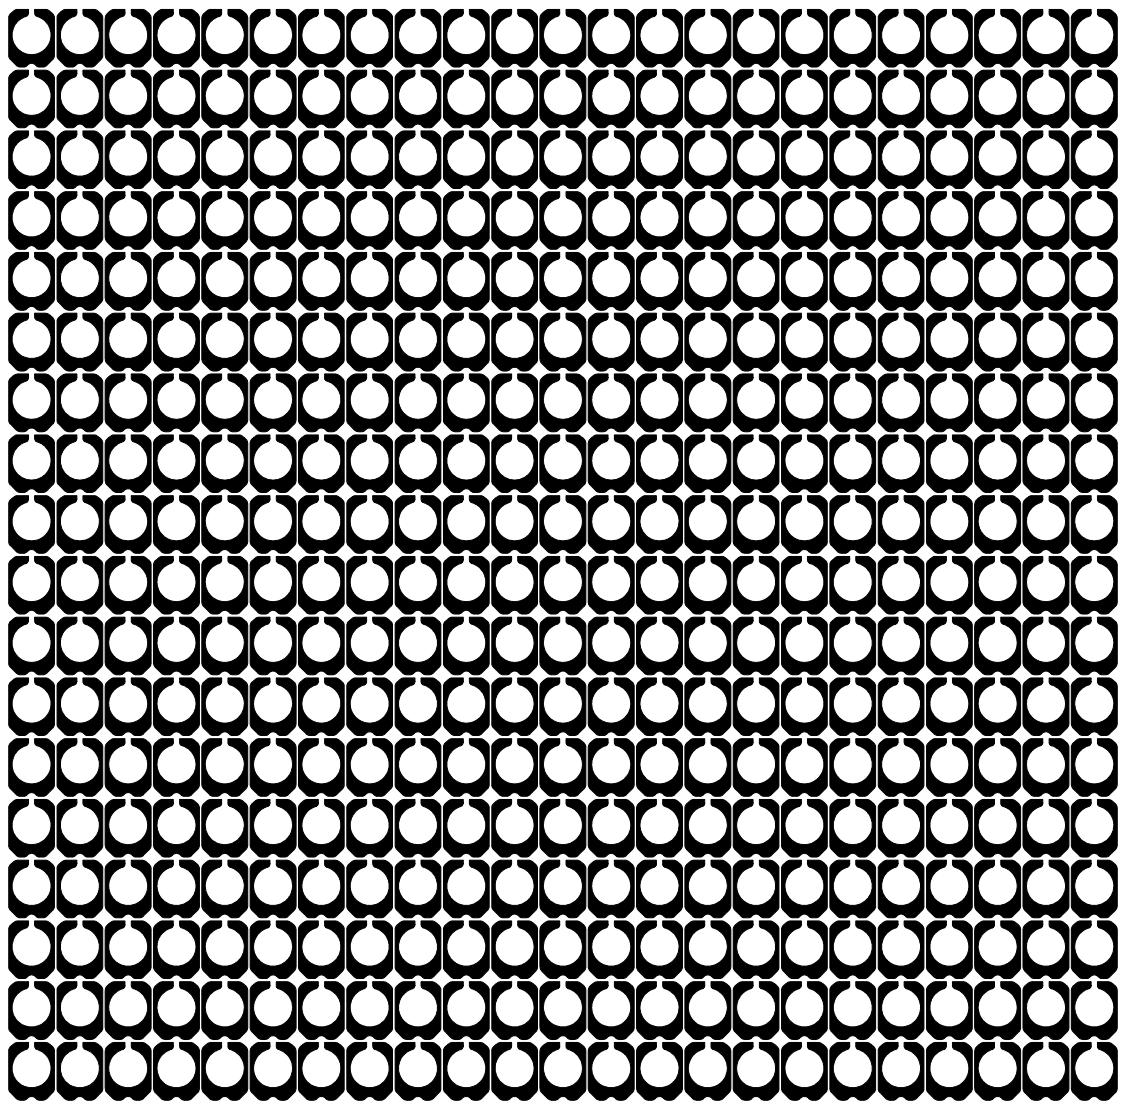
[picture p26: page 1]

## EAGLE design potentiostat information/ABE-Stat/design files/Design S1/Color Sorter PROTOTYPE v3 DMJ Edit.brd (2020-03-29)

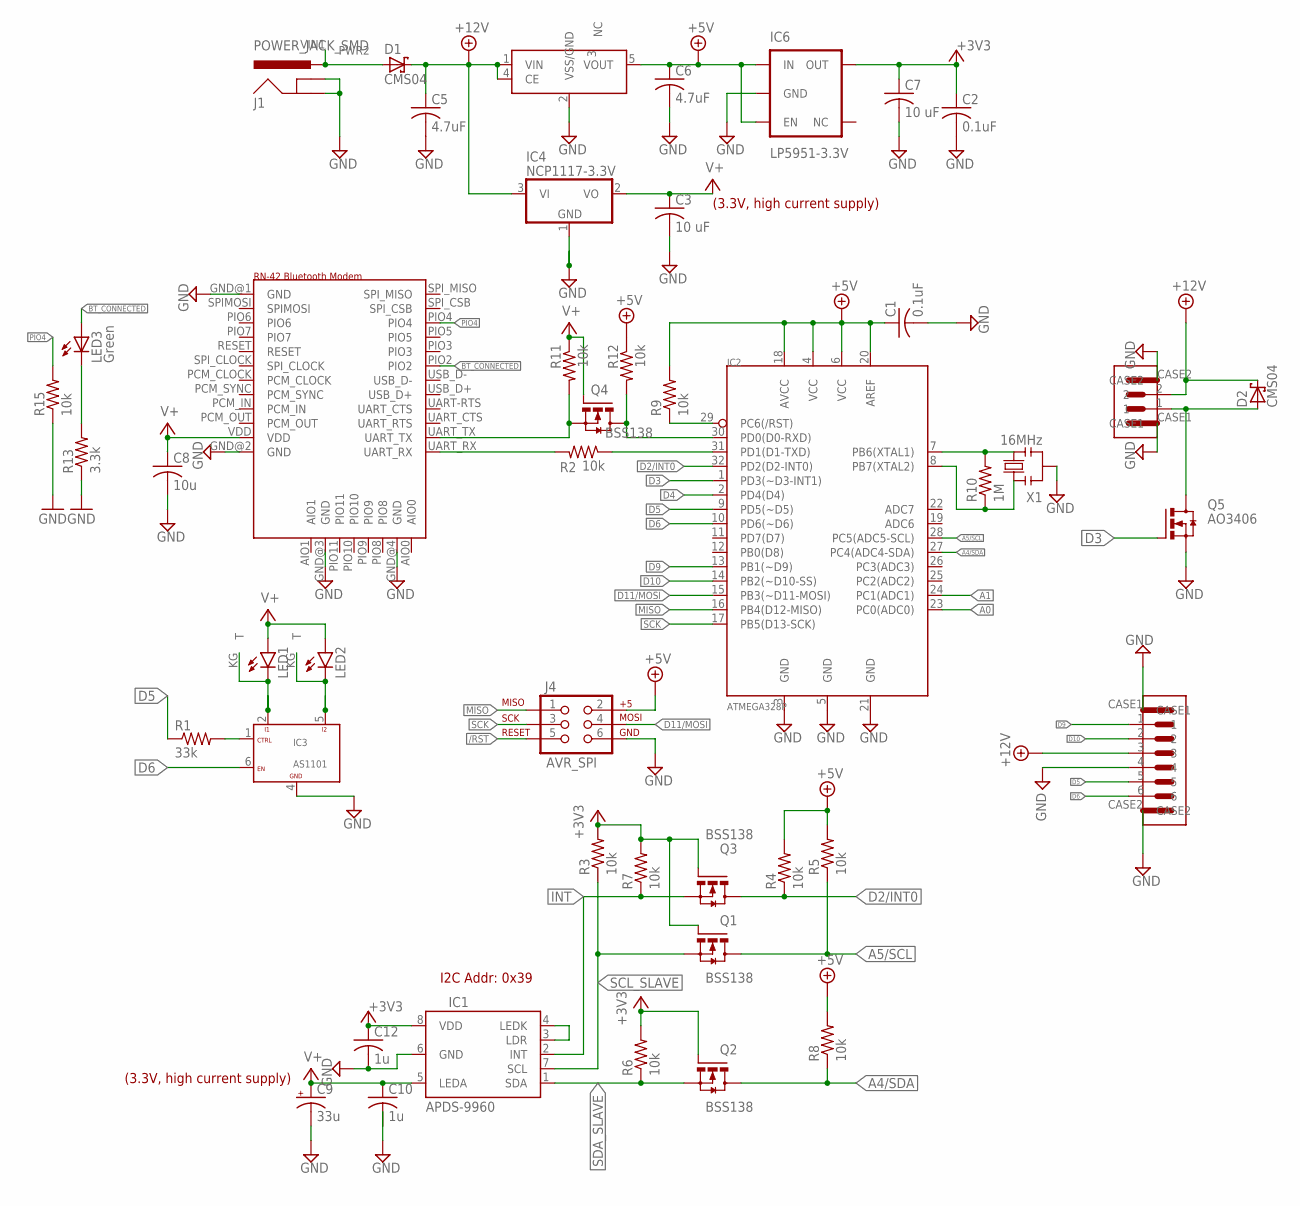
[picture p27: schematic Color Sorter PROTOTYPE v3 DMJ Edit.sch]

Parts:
A1: RN-42_BLUETOOTH; RN-42
C1, C2: 0.1uF; C0805
C3, C7: 10 uF; C0805
C5, C6: 4.7uF; C0805
C8: 10u; C0805
C9: 33u; CT7343
C10, C12: 1u; C0805
D1, D2: CMS04; 3-4E1A
IC1: APDS-9960; SPARKFUN-SENSORS_APDS-9960
IC2: ATMEGA328P; TQFP-32
IC3: AS1101; SC70-6
IC4: NCP1117-3.3V; SOT-223
IC5: XC6701-5V; DMJ_LINEAR_SOT23-5
IC6: LP5951-3.3V; SOT23-5
J1: POWER_JACK_SMD; SMD_POWER_JACK
J4: AVR_SPI; 2X3
LED1, LED2: LED_SAMSUNG_SPMWHT541MD7WATMS0
LED3: Green; LED-1206
Q1, Q2, Q3, Q4: BSS138; BE-420-CUSTOM-PARTS_SOT-23
Q5: AO3406; SOT-23-3
R1: 33k; R0805
R2, R3, R4, R5, R6, R7, R8, R9, R11, R12, R15: 10k; R0805
R10: 1M; R0805
R13: 3.3k; R0805
U$4: 1A-JENKINS-PHOENIX-CONTACT-CONNECTORS_1A_JENKINS_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; 1A-JENKINS-PHOENIX-CONTACT-CONNECTORS_1A_JENKINS_2013_6-PIN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
U$7: 1A_JENKINS_2013_2PIN_SMD_PHOENIX_CONTACT; 1A_JENKINS_2013_2-PIN-R/A_PHOENIX_SMD
X1: 16MHz; 1A_JENKINS_2013_RESONATOR_SMD

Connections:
+3V3: C2.1, C7.1, C12.1, IC1.8 (VDD), IC6.5 (OUT), Q1.1-G (G), Q2.1-G (G), Q3.1-G (G), R3.2, R6.2, R7.2
+5V: C1.1, C6.1, IC2.4 (VCC), IC2.6 (VCC), IC2.18 (AVCC), IC2.20 (AREF), IC5.5 (VOUT), IC6.1 (IN), IC6.3 (EN), J4.2, R4.2, R5.2, R8.2, R9.2, R12.1
+12V: C5.1, D1.C, D2.C, IC4.3 (VI), IC5.1 (VIN), IC5.4 (CE), U$4.3, U$7.2
/RST: IC2.29 (PC6(/RST)), J4.5, R9.1
A0: IC2.23 (PC0(ADC0))
A1: IC2.24 (PC1(ADC1))
A4/SDA: IC2.27 (PC4(ADC4-SDA)), Q2.3-D (D), R8.1
A5/SCL: IC2.28 (PC5(ADC5-SCL)), Q1.3-D (D), R5.1
BT_CONNECTED: A1.PIO2, LED3.A
D2/INT0: IC2.32 (PD2(D2-INT0)), Q3.3-D (D), R4.1
D3: IC2.1 (PD3(~D3-INT1)), Q5.1 (G)
D4: IC2.2 (PD4(D4))
D5: IC2.9 (PD5(~D5)), R1.1, U$4.5
D6: IC2.10 (PD6(~D6)), IC3.6 (EN), U$4.6
D9: IC2.13 (PB1(~D9)), U$4.1
D10: IC2.14 (PB2(~D10-SS)), U$4.2
D11/MOSI: IC2.15 (PB3(~D11-MOSI)), J4.4
GND: A1.GND@1 (GND), A1.GND@2 (GND), A1.GND@3 (GND), A1.GND@4 (GND), C1.2, C2.2, C3.2, C5.2, C6.2, C7.2, C8.2, C9.-, C10.2, C12.2, IC1.6 (GND), IC2.3 (GND), IC2.5 (GND), IC2.21 (GND), IC3.4 (GND), IC4.1 (GND), IC5.2 (VSS/GND), IC6.2 (GND), J1.GND, J1.P$4 (GNDBREAK), J4.6, Q5.2 (S), R13.1, R15.1, U$4.4, U$4.CASE1, U$4.CASE2, U$7.CASE1, U$7.CASE2, X1.2
INT: IC1.2 (INT), Q3.2-S (S), R7.1
MISO: IC2.16 (PB4(D12-MISO)), J4.1
unnamed: IC2.31 (PD1(D1-TXD)), R2.1
unnamed: IC1.3 (LDR), IC1.4 (LEDK)
unnamed: IC2.7 (PB6(XTAL1)), R10.2, X1.3
unnamed: IC3.2 (I1), LED1.KA (C), LED1.KG (T)
unnamed: IC3.5 (I2), LED2.KA (C), LED2.KG (T)
unnamed: A1.UART_RX, R2.2
unnamed: IC2.8 (PB7(XTAL2)), R10.1, X1.1
unnamed: D2.A, Q5.3 (D), U$7.1
unnamed: A1.UART_TX, Q4.2-S (S), R11.2
unnamed: IC2.30 (PD0(D0-RXD)), Q4.3-D (D), R12.2
unnamed: LED3.C, R13.2
unnamed: IC3.1 (CTRL), R1.2
PIO4: A1.PIO4, R15.2
SCK: IC2.17 (PB5(D13-SCK)), J4.3
SCL_SLAVE: IC1.7 (SCL), Q1.2-S (S), R3.1
SDA_SLAVE: IC1.1 (SDA), Q2.2-S (S), R6.1
USB_VIN: D1.A, J1.VIN0 (PWR), J1.VIN1 (PWR2)
V+: A1.VDD, C3.1, C8.1, C9.+, C10.1, IC1.5 (LEDA), IC4.2 (VO), LED1.A, LED2.A, Q4.1-G (G), R11.1

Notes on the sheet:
I2C Addr: 0x39
(3.3V, high current supply)

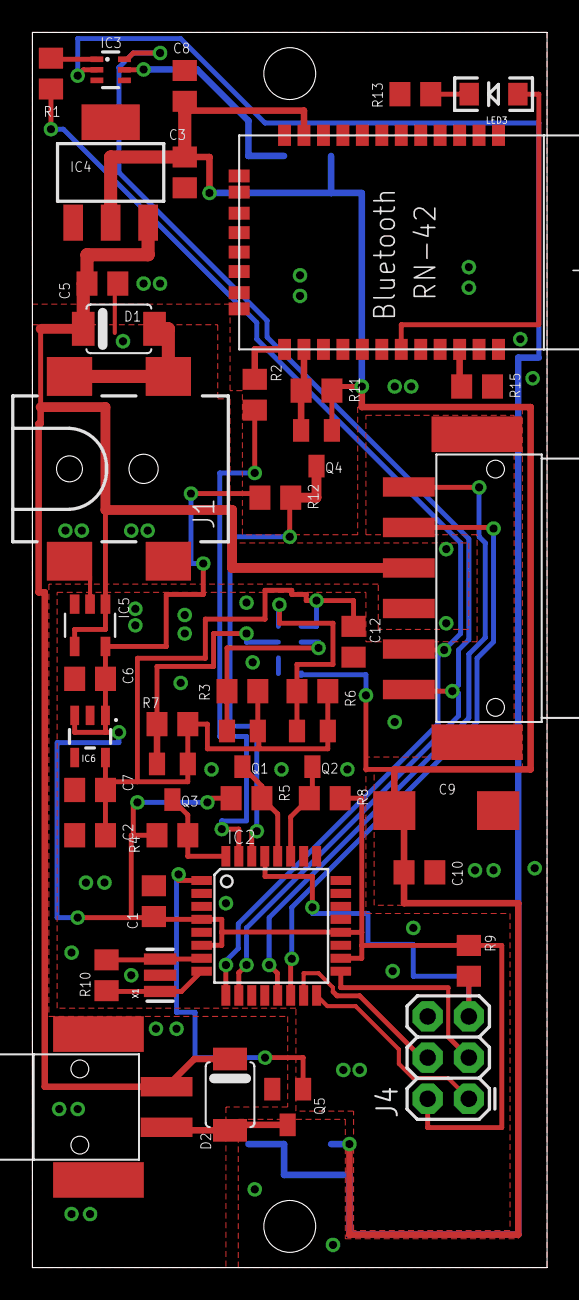
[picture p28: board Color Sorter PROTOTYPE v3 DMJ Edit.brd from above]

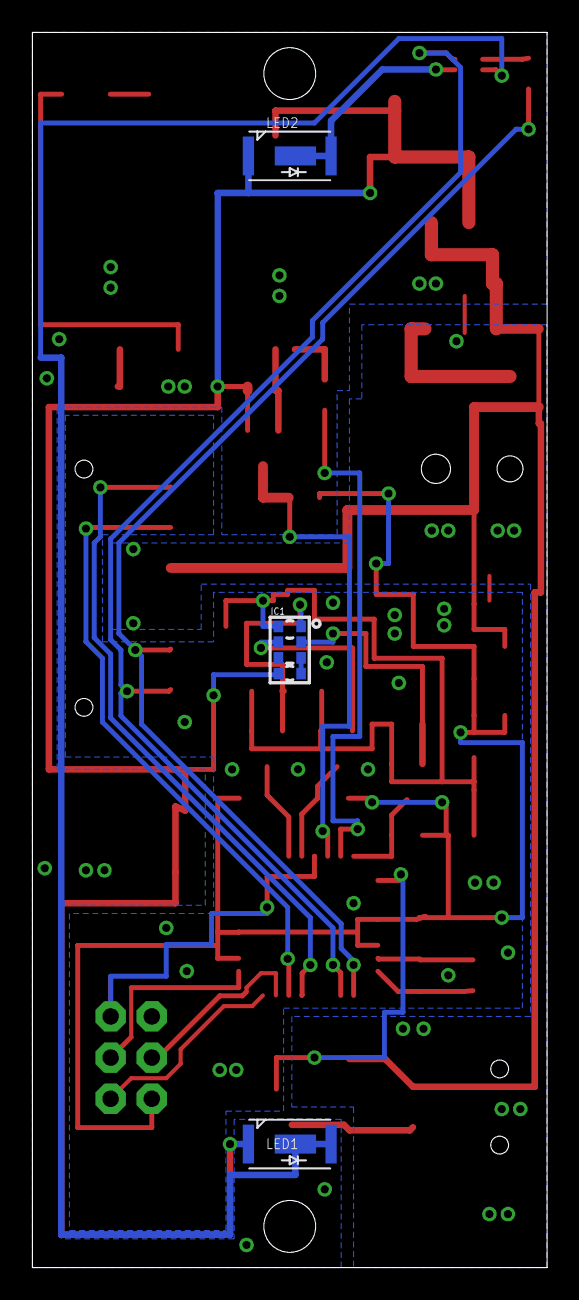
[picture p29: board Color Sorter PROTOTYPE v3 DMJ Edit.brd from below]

Board: 2 copper layers, 31.8 x 76.2 mm, 46 parts (3 on the bottom side), 35 nets.

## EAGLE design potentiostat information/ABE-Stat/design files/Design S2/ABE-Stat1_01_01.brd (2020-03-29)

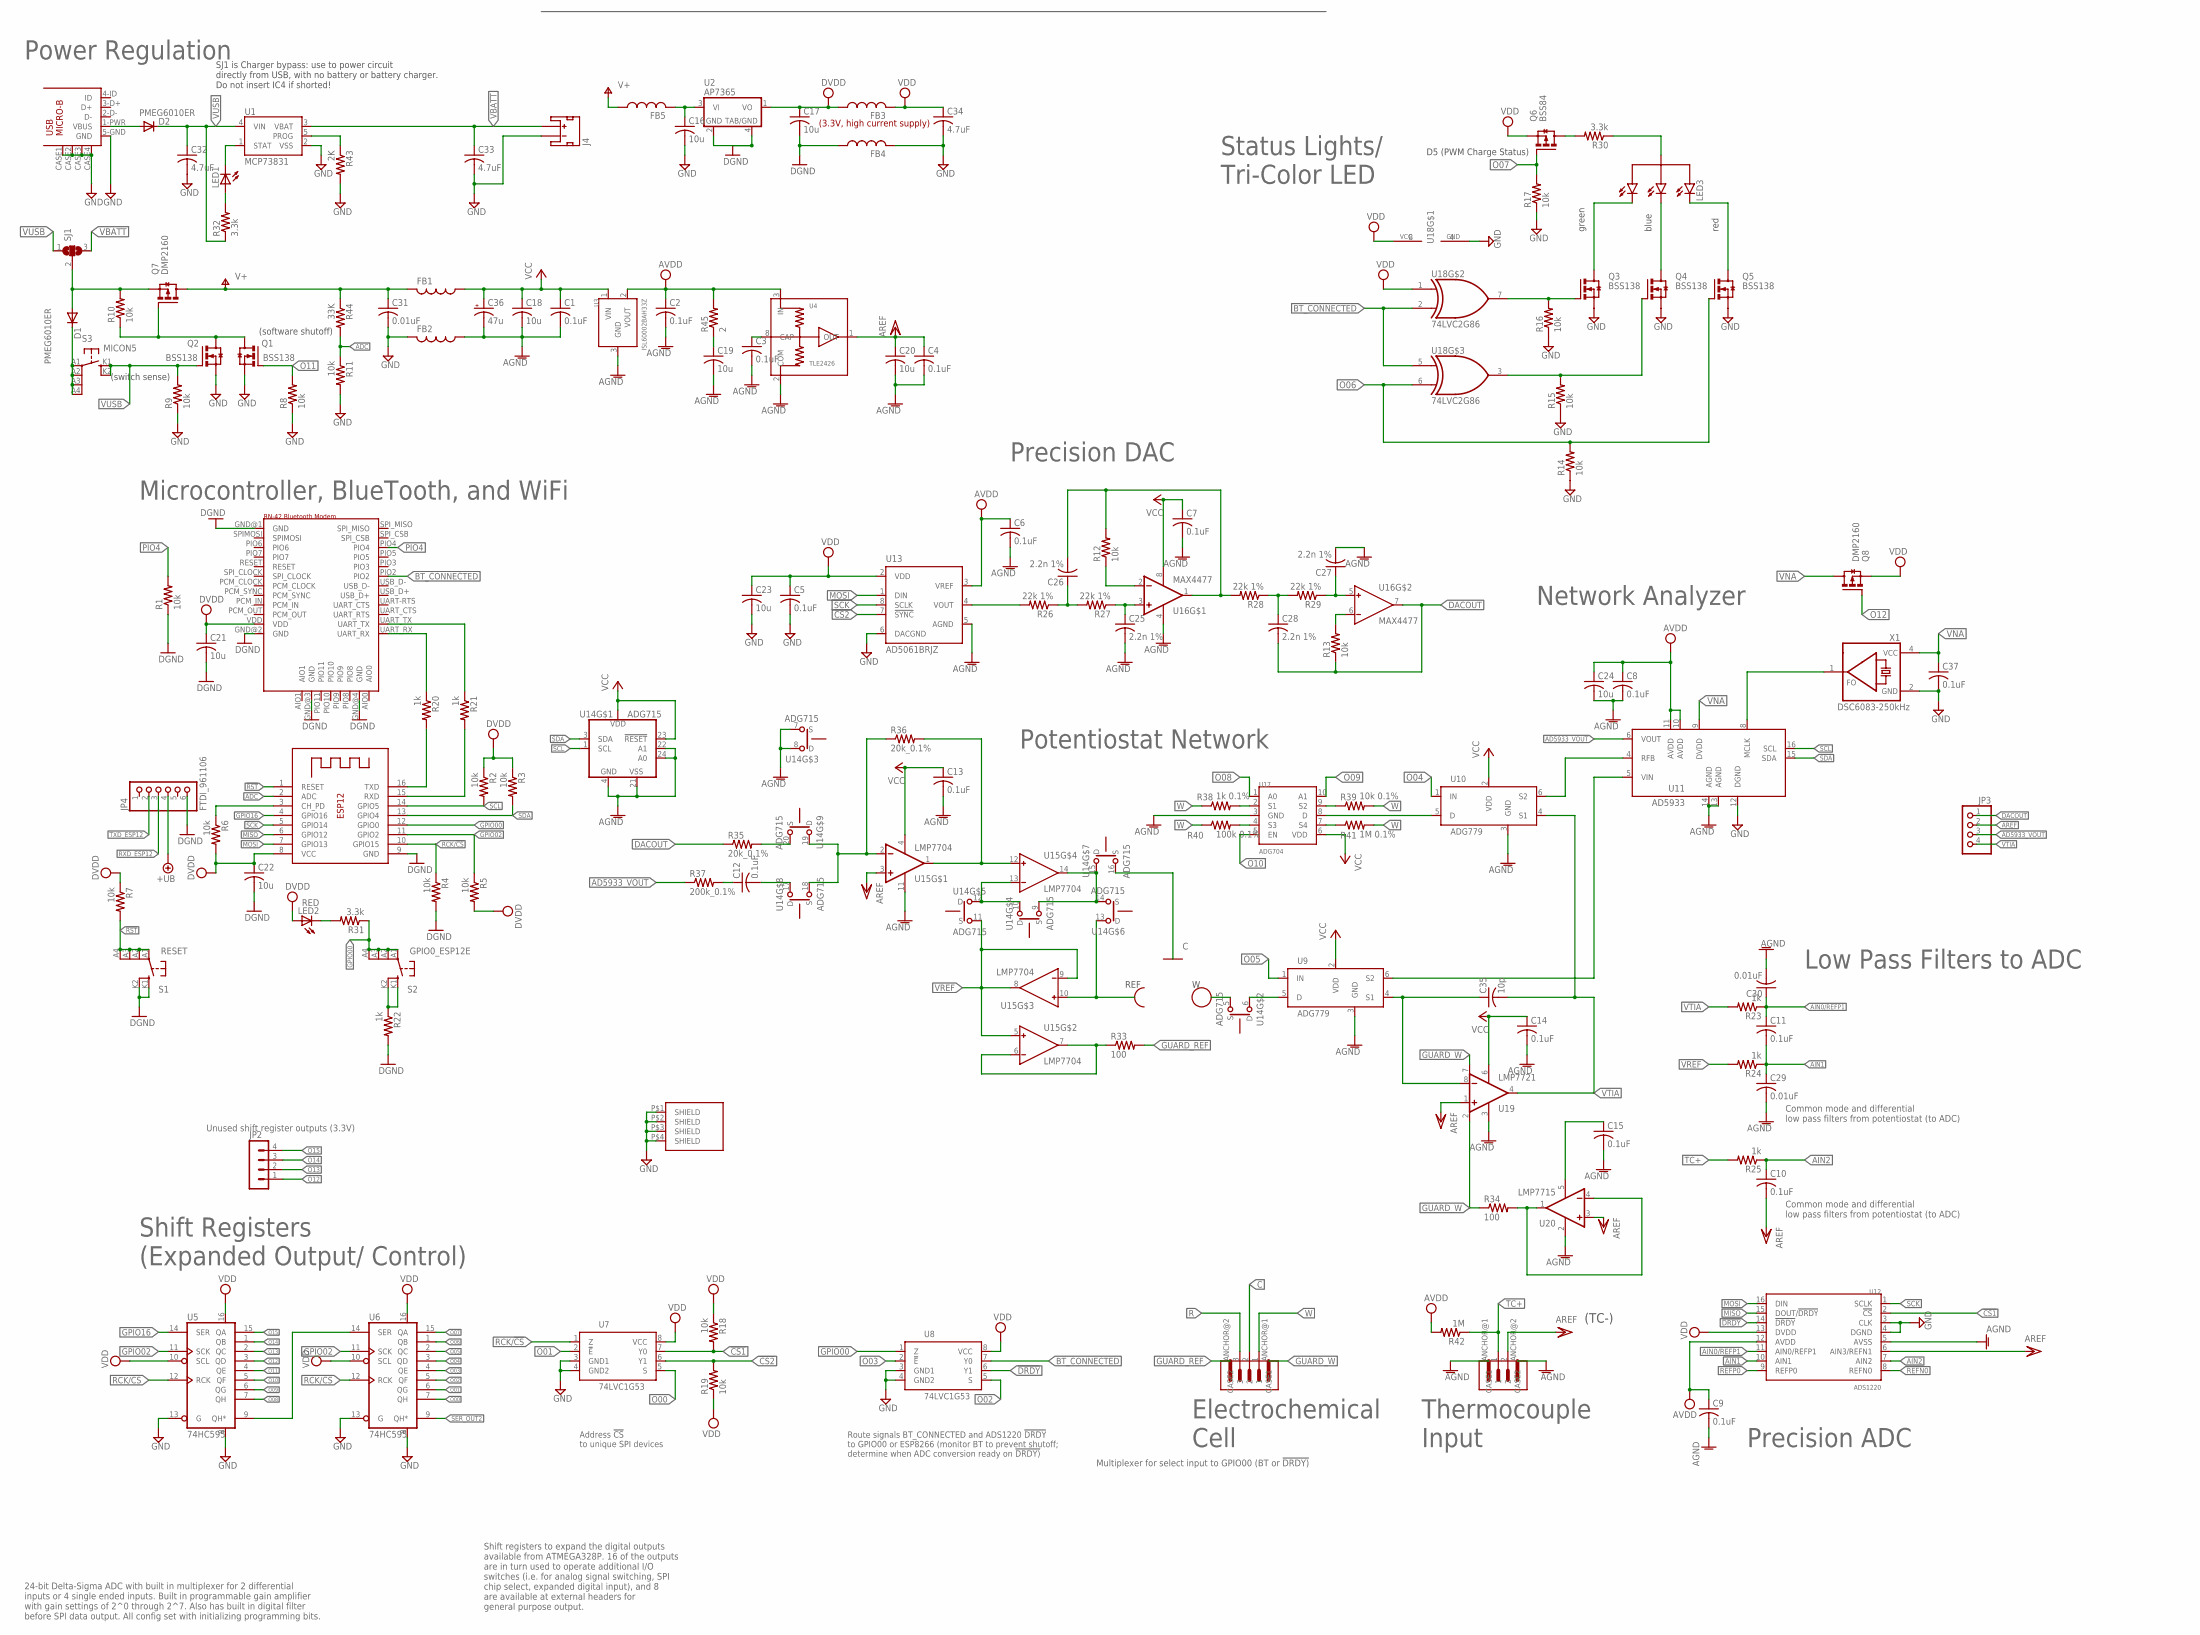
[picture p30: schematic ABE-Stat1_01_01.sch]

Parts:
A1: ESP-12E; ESP-12
A2: RN-42_BLUETOOTH; RN-42
C1, C2, C3, C4, C5, C6, C7, C8, C9, C10, C11, C12, C13, C14, C15, C37: 0.1uF; C0805
C16, C17, C18, C19, C20, C21, C22, C23, C24: 10u; C0805
C25, C26, C27, C28: 2.2n 1%; C0805
C29, C30, C31: 0.01uF; C0805
C32, C33, C34: 4.7uF; C0805
C35: 10p; C0805
C36: 47u; D/7343-31W
D1, D2: PMEG6010ER; DIODE_SOD123
FB1, FB2, FB3, FB4, FB5: FERRITE_BEAD_5A_0805; R0805
J1: 1A_JENKINS_2013_3PIN_SMD_PHOENIX_CONTACTVERTICAL; 3-PIN-VERT_PHOENIX_SMD
J2: 1A_JENKINS_2013_2PIN_SMD_PHOENIX_CONTACTVERTICAL; 2-PIN-VERT_PHOENIX_SMD
J3: USB-MICRO-B; USB_MICRO_B_WURTH_629105136821
J4: JST_2MM_MALE; JST-2-SMD
JP2: MA04-1
JP3: PINHD-1X4; 1X04
JP4: FTDI_961106; 6_PIN_0.1IN_STRAIGHT_HEADER
LED1: LEDCHIPLED_1206; CHIPLED_1206
LED2: RED; LED-1206
LED3: LED_RBG_COM_ANODE; LED_RGB_WURTH_150141M173100
Q1, Q2, Q3, Q4, Q5: BSS138; SOT-23
Q6: BSS84; SOT-23-3
Q7, Q8: DMP2160; SOT-23-3
R1, R2, R3, R4, R5, R6, R7, R8, R9, R10, R11, R12, R13, R14, R15, R16, R17, R18, R19: 10k; R0805
R20, R21, R22, R23, R24, R25: 1k; R0805
R26, R27, R28, R29: 22k 1%; R0805
R30, R31, R32: 3.3k; R0805
R33, R34: 100; R0805
R35, R36: 20k_0.1%; R0805
R37: 200k_0.1%; R0805
R38: 1k 0.1%; R0805
R39: 10k 0.1%; R0805
R40: 100k 0.1%; R0805
R41: 1M 0.1%; R0805
R42: 1M; R0805
R43: 2K; R0805
R44: 33K; R0805
R45: 2; R2512
S1: RESET; RAFI-MICON5_SWITCH
S2: GPIO0_ESP12E; RAFI-MICON5_SWITCH
S3: MICON5; RAFI-MICON5_SWITCH
SH1: SMARTDART_SHIELD; SMARTDART-SHIELD
SJ1: SJ2W; SJ_2
U1: MCP73831; SOT23-5
U2: AP7365; SOT-223
U3: ISL60002BAH33Z; SOT-23-3
U4: TLE2426; SOIC-8
U5, U6: 74HC595; TSSOP16
U7, U8: 74LVC1G53; VSSOP8
U9, U10: ADG779; SC70-6
U11: AD5933; SSOP-16
U12: ADS1220; TSSOP16
U13: AD5061BRJZ; SOT-23-8
U14: ADG715; TSSOP24
U15: LMP7704; TSSOP14
U16: MAX4477; UMAX8
U17: ADG704; MSOP10
U18: 74LVC2G86; US-8
U19: LMP7721; SOIC-8
U20: LMP7715; SOT23-5
X1: DSC6083-250kHz; DSC60XX_OSCILLATOR_3.2X2.5MM

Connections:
!CS1: R18.2, U7.7 (Y0), U12.2 (!CS)
!CS2: R19.2, U7.6 (Y1), U13.7 (!SYNC)
!DRDY: U8.6 (Y1), U12.14 (!DRDY)
!RST: A1.1 (RESET), R7.2, S1.A1, S1.A2 (P1), S1.A3 (P2), S1.A4 (P3)
+UB: JP4.4
AD5933_VIN: U9.6 (S2), U11.5 (VIN)
AD5933_VOUT: JP3.3, R37.1, U11.6 (VOUT)
ADC: A1.2 (ADC), R11.1, R44.2
AGND: C1.2, C2.2, C3.2, C4.2, C6.2, C7.2, C8.2, C9.2, C13.2, C14.2, C15.2, C18.2, C19.2, C20.2, C24.2, C25.2, C27.2, C29.2, C30.2, C36.-, FB2.1, J2.ANCHOR@1 (CASE1), J2.ANCHOR@2 (CASE2), U3.3 (GND), U4.2 (COM), U9.3 (GND), U10.3 (GND), U11.13 (AGND), U11.14 (AGND), U12.5 (AVSS), U13.5 (AGND), U14.4 (GND), U14.7 (S), U14.8 (D), U14.21 (VSS), U14.22 (A1), U14.24 (A0), U15.11 (V-), U16.4 (V-), U17.3 (GND), U19.3 (V-), U20.2 (V-)
AIN0/REFP1: C11.1, C30.1, R23.1, U12.11 (AIN0/REFP1)
AIN1: C11.2, C29.1, R24.1, U12.10 (AIN1)
AIN2: C10.1, R25.1, U12.7 (AIN2)
AREF: C4.1, C10.2, C20.1, J2.2, JP3.2, U4.1 (OUT), U12.6 (AIN3/REFN1), U15.3 (+IN), U19.1 (+IN), U20.3 (+IN)
AVDD: C2.1, C6.1, C8.1, C9.1, C24.1, R42.2, R45.2, U3.2 (VOUT), U4.3 (IN), U11.10 (AVDD), U11.11 (AVDD), U12.12 (AVDD), U13.3 (VREF)
BT_CONNECTED: A2.PIO2, U8.7 (Y0), U18.2 (I1), U18.5 (I0)
C: J1.2, U14.16 (S)
DACOUT: C28.2, JP3.1, R13.1, R35.1, U16.7 (OUT)
DGND: A1.9 (GND), A2.GND@1 (GND), A2.GND@2 (GND), A2.GND@3 (GND), A2.GND@4 (GND), C17.2, C21.2, C22.2, FB4.1, JP4.6, R1.1, R4.2, R22.2, S1.K1 (S), S1.K2 (S1), U2.2 (GND), U2.4 (GND1)
DVDD: A1.8 (VCC), A2.VDD, C17.1, C21.1, C22.1, FB3.1, LED2.A, R2.1, R3.1, R5.2, R6.2, R7.1, U2.1 (VO)
GND: C5.2, C16.2, C23.2, C31.2, C32.2, C33.2, C34.2, C37.2, FB2.2, FB4.2, J3.5-GND (GND), J3.CASE1 (CASE), J3.CASE2 (CASE), J3.CASE3 (CASE), J3.CASE4 (CASE), J4.1 (-), Q1.2-S (S), Q2.2-S (S), Q3.2-S (S), Q4.2-S (S), Q5.2-S (S), R8.1, R9.1, R11.2, R14.1, R15.1, R16.1, R17.1, R43.2, SH1.P$1, SH1.P$2, SH1.P$3, SH1.P$4, U1.2 (VSS), U5.8 (GND), U5.13 (G), U6.8 (GND), U6.13 (G), U7.3 (GND1), U7.4 (GND2), U8.3 (GND1), U8.4 (GND2), U11.12 (DGND), U12.3 (CLK), U12.4 (DGND), U13.6 (DACGND), U18.4 (GND), X1.2 (GND)
GPIO00: A1.12 (GPIO0), R31.1, S2.A1, S2.A2 (P1), S2.A3 (P2), S2.A4 (P3), U8.1 (Z)
GPIO02: A1.11 (GPIO2), R5.1, U5.11 (SCK), U6.11 (SCK)
GPIO16: A1.4 (GPIO16), U5.14 (SER)
GUARD_REF: J1.ANCHOR@2 (CASE2), R33.2
GUARD_W: J1.ANCHOR@1 (CASE1), R34.1, U19.2 (GUARD), U19.7 (GUARD)
MISO: A1.6 (GPIO12), U12.15 (DOUT/!DRDY)
MOSI: A1.7 (GPIO13), U12.16 (DIN), U13.1 (DIN)
unnamed: A2.UART_RX, R20.1
unnamed: U14.10 (D), U14.12 (D), U15.13 (IN-)
unnamed: D2.A, J3.1-PWR (VBUS)
unnamed: A2.UART_TX, R21.1
unnamed: Q3.1-G (G), R16.2, U18.7 (O)
unnamed: U9.5 (D), U14.6 (D)
unnamed: R43.1, U1.5 (PROG)
unnamed: U5.9 (QH*), U6.14 (SER)
unnamed: C25.1, R27.1, U16.3 (+IN)
unnamed: LED1.C, U1.1 (STAT)
unnamed: R26.2, U13.4 (VOUT)
unnamed: LED1.A, R32.2
unnamed: C19.1, R45.1
unnamed: C12.1, R37.2
unnamed: C26.1, R26.1, R27.2
unnamed: R22.1, S2.K1 (S), S2.K2 (S1)
unnamed: Q4.1-G (G), R15.2, U18.3 (O)
unnamed: D1.C, S3.A1, S3.A2 (P1), S3.A3 (P2), S3.A4 (P3)
unnamed: C3.1, U4.8 (CAP)
unnamed: C26.2, R12.2, R28.2, U16.1 (OUT)
unnamed: C28.1, R28.1, R29.2
unnamed: C27.1, R29.1, U16.5 (IN+)
unnamed: R12.1, U16.2 (-IN)
unnamed: U14.9 (S), U14.14 (S), U14.15 (D), U15.14 (OUT)
unnamed: R13.2, U16.6 (IN-)
unnamed: LED2.C, R31.2
unnamed: C12.2, U14.17 (D)
unnamed: C35.1, U9.4 (S1), U19.8 (-IN)
unnamed: R36.1, U14.18 (S), U14.19 (D), U15.2 (-IN)
unnamed: R36.2, U15.1 (OUT), U15.12 (IN+)
unnamed: U10.6 (S2), U11.4 (RFB)
unnamed: R41.1, U17.7 (S4)
unnamed: R33.1, U15.6 (IN-), U15.7 (OUT)
unnamed: R39.1, U17.9 (S2)
unnamed: Q1.3-D (D), Q2.3-D (D), Q7.1 (G), R10.1
unnamed: U10.5 (D), U17.8 (D)
unnamed: R38.2, U17.2 (S1)
unnamed: R40.2, U17.4 (S3)
unnamed: LED3.G, Q3.3-D (D)
unnamed: R34.2, U20.1 (OUT), U20.4 (-IN)
unnamed: LED3.B, Q4.3-D (D)
unnamed: LED3.R, Q5.3-D (D)
unnamed: Q6.3 (D), R30.2
unnamed: LED3.A, R30.1
unnamed: R35.2, U14.20 (S)
unnamed: C16.1, FB5.2, U2.3 (VI)
unnamed: A1.3 (CH_PD), R6.1
unnamed: U11.8 (MCLK), X1.1 (FO)
unnamed: D1.A, Q7.2 (S), R10.2, SJ1.2
O00: U6.7 (QH), U7.5 (S)
O01: U6.6 (QG), U7.2 (!E)
O02: U6.5 (QF), U8.5 (S)
O03: U6.4 (QE), U8.2 (!E)
O04: U6.3 (QD), U10.1 (IN)
O05: U6.2 (QC), U9.1 (IN)
O06: Q5.1-G (G), R14.2, U6.1 (QB), U18.6 (I1)
O07: Q6.1 (G), R17.2, U6.15 (QA)
O08: U5.7 (QH), U17.1 (A0)
O09: U5.6 (QG), U17.10 (A1)
O10: U5.5 (QF), U17.5 (EN)
O11: Q1.1-G (G), R8.2, U5.4 (QE)
O12: JP2.1, Q8.1 (G), U5.3 (QD)
O13: JP2.2, U5.2 (QC)
O14: JP2.3, U5.1 (QB)
O15: JP2.4, U5.15 (QA)
PIO4: A2.PIO4, R1.2
R: J1.3, U14.13 (D), U15.10 (IN+)
RCK/!CS: A1.10 (GPIO15), R4.1, U5.12 (RCK), U6.12 (RCK), U7.1 (Z)
REFN0: U12.8 (REFN0)
REFP0: U12.9 (REFP0)
RXD_ESP12: A1.15 (RXD), JP4.3, R21.2
SCK: A1.5 (GPIO14), U12.1 (SCLK), U13.8 (SCLK)
SCL: A1.14 (GPIO5), R2.2, U11.16 (SCL), U14.1 (SCL)
SDA: A1.13 (GPIO4), R3.2, U11.15 (SDA), U14.3 (SDA)
SER_OUT2: U6.9 (QH*)
TC+: J2.1, R25.2, R42.1
TXD_ESP12: A1.16 (TXD), JP4.2, R20.2
V+: C31.1, FB1.2, FB5.1, Q7.3 (D), R44.1
VBATT: C33.1, J4.2 (+), SJ1.3, U1.3 (VBAT)
VCC: C1.1, C7.1, C13.1, C14.1, C15.1, C18.1, C36.+, FB1.1, U3.1 (VIN), U9.2 (VDD), U10.2 (VDD), U14.2 (VDD), U14.23 (!RESET), U15.4 (V+), U16.8 (V+), U17.6 (VDD), U19.6 (V+), U20.5 (V+)
VDD: C5.1, C23.1, C34.1, FB3.2, Q6.2 (S), Q8.2 (S), R18.1, R19.1, U5.10 (SCL), U5.16 (VCC), U6.10 (SCL), U6.16 (VCC), U7.8 (VCC), U8.8 (VCC), U12.13 (DVDD), U13.2 (VDD), U18.1 (I0), U18.8 (VCC)
VNA: C37.1, Q8.3 (D), U11.9 (DVDD), X1.4 (VCC)
VREF: R24.2, U14.11 (S), U15.5 (IN+), U15.8 (OUT), U15.9 (IN-)
VTIA: C35.2, JP3.4, R23.2, U10.4 (S1), U19.4 (OUT)
VUSB: C32.1, D2.C, Q2.1-G (G), R9.2, R32.1, S3.K1 (S), S3.K2 (S1), SJ1.1, U1.4 (VIN)
W: J1.1, R38.1, R39.2, R40.1, R41.2, U14.5 (S)

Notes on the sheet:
(3.3V, high current supply)
Route signals BT_CONNECTED and ADS1220 !DRDY to GPIO00 or ESP8266 (monitor BT to prevent shutoff; determine when ADC conversion ready on !DRDY)
Shift registers to expand the digital outputs available from ATMEGA328P. 16 of the outputs are in turn used to operate additional I/O switches (i.e. for analog signal switching, SPI chip select, expanded digital input), and 8 are available at external headers for general purpose output.
Multiplexer for select input to GPIO00 (BT or !DRDY)
Power Regulation
Microcontroller, BlueTooth, and WiFi
Precision ADC
Shift Registers (Expanded Output/ Control)
24-bit Delta-Sigma ADC with built in multiplexer for 2 differential inputs or 4 single ended inputs. Built in programmable gain amplifier with gain settings of 2^0 through 2^7. Also has built in digital filter before SPI data output. All config set with initializing programming bits.
Common mode and differential low pass filters from potentiostat (to ADC)
Address !CS to unique SPI devices
(switch sense)
(software shutoff)
Precision DAC
Network Analyzer
Potentiostat Network
Low Pass Filters to ADC
Thermocouple Input
Electrochemical Cell
D5 (PWM Charge Status)
green
blue
red
Status Lights/ Tri-Color LED
(TC-)
Unused shift register outputs (3.3V)
REF
SJ1 is Charger bypass: use to power circuit directly from USB, with no battery or battery charger. Do not insert IC4 if shorted!

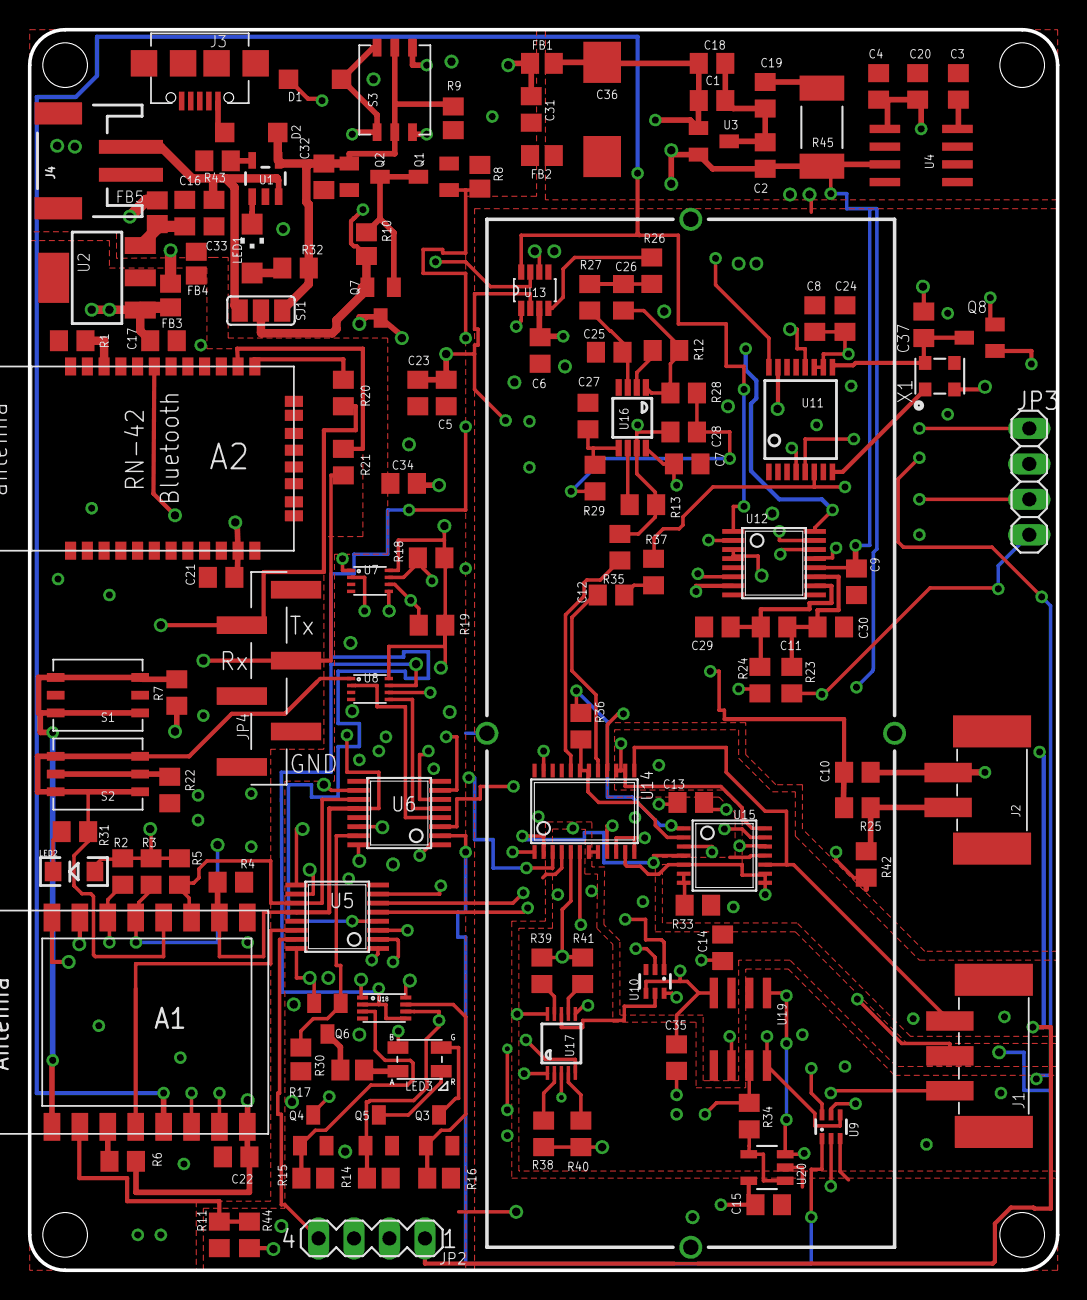
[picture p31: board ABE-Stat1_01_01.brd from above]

Board: 4 copper layers, 73.7 x 88.9 mm, 135 parts (0 on the bottom side), 109 nets.

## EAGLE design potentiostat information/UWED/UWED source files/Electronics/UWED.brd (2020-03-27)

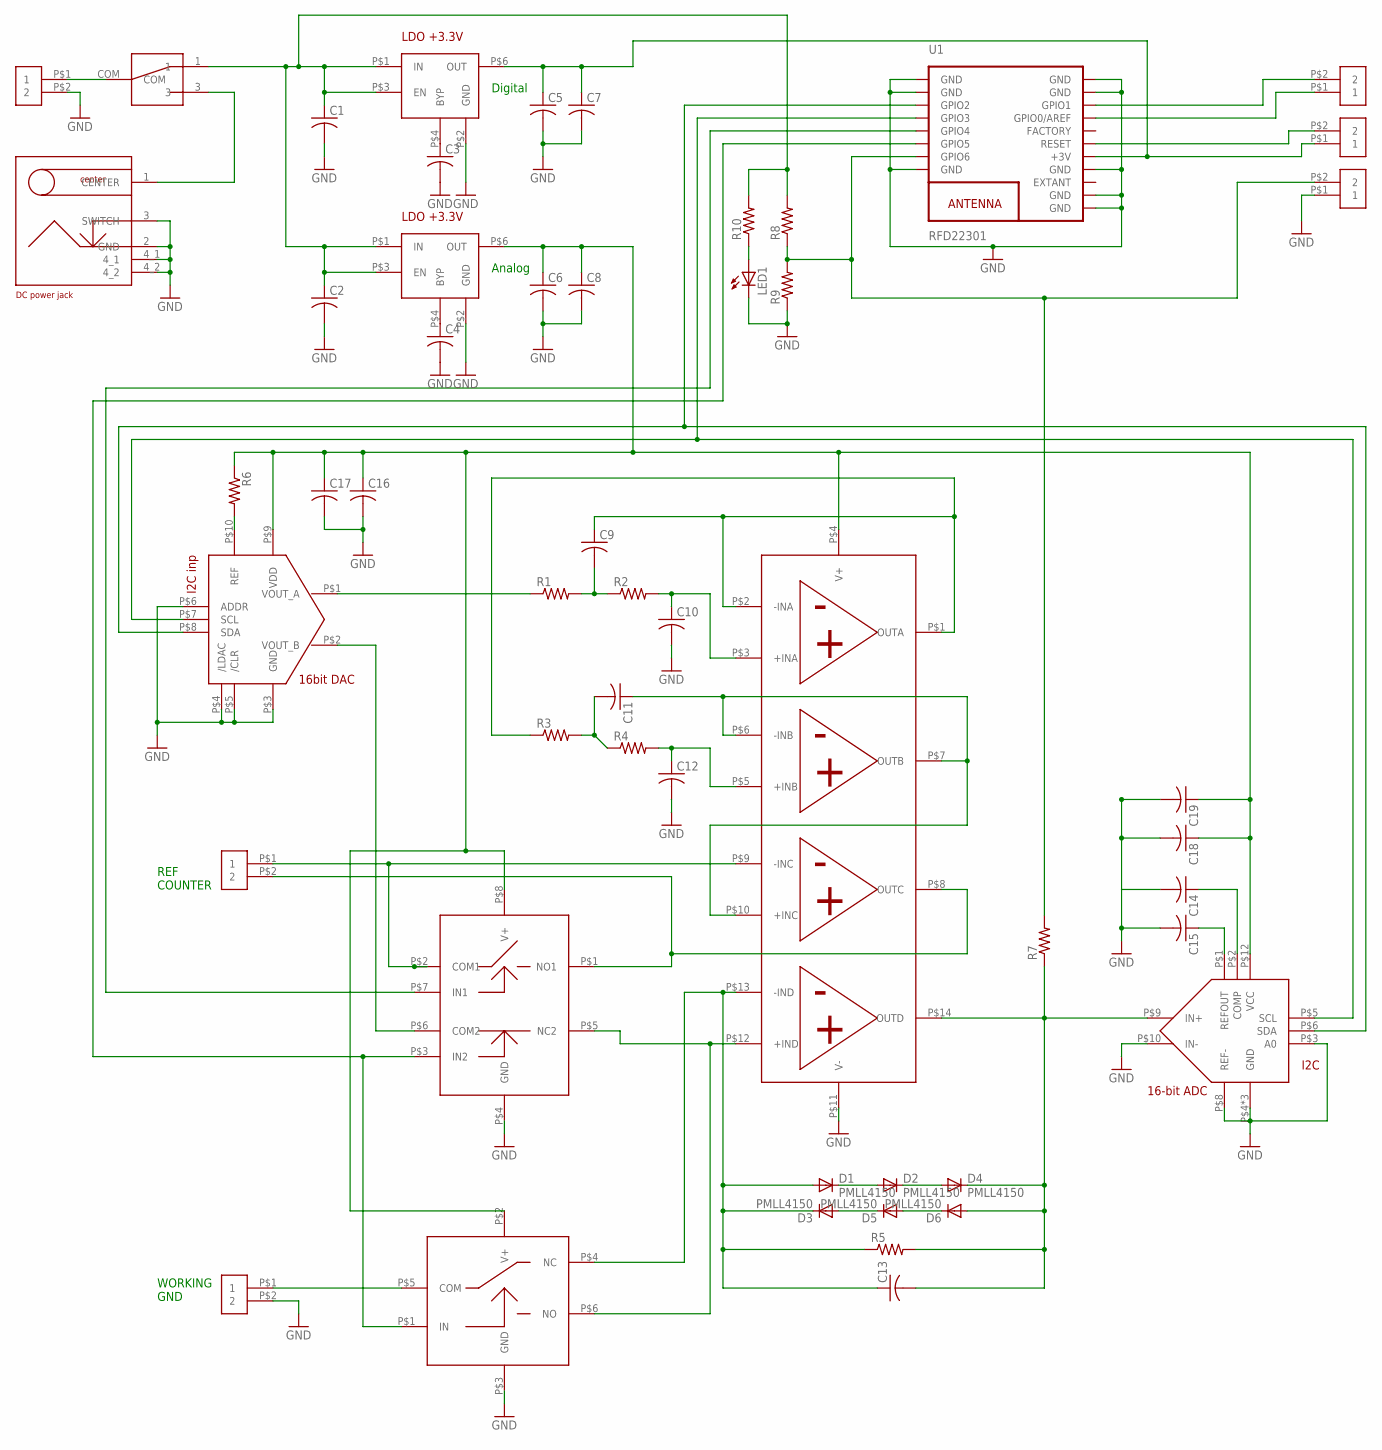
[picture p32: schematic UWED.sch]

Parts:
C1, C2, C3, C4, C5, C6, C7, C8, C9, C10, C11, C12, C13, C14, C15, C16, C17, C18, C19: C-USC0805; C0805
D1, D2, D3, D4, D5, D6: PMLL4150; SOD80C
LED1: LEDSML0805; SML0805
R1, R2, R3, R4, R5, R6, R7, R8, R9, R10: R-US_R0805; R0805
U1: RFD22301
U$1: 4OPAMPS-AD8608ARUZ; MSOP14_0.65MM
U$2: ADC_LTC2471IMS; MSOP12_0.65MM
U$3, U$4, U$5, U$6, U$7, U$15: CONTACT_PADS_SMD_2
U$8: DAC_AD5667RBRMZ-2; MSOP10_0.5MM
U$9: DC_JACK_0.7MM; PJ-032H-SMT
U$10, U$11: LDO-MIC5205-3.3YM5-TR; SOT-23-6
U$12: SWITCH_MAX4643EUA; MSOP8_0.65MM
U$13: SWITCH_MAX4644EUT; SOT-23-6
U$14: SW_TOGGLELARGE; TOGGLE_34E

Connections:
GND: C1.2, C2.2, C3.2, C4.2, C5.2, C6.2, C7.2, C8.2, C10.2, C12.2, C14.2, C15.2, C16.2, C17.2, C18.2, C19.2, LED1.C, R9.1, U1.1 (GND), U1.2 (GND), U1.8 (GND), U1.9 (GND), U1.10 (GND), U1.12 (GND), U1.18 (GND), U1.19 (GND), U$1.P$11 (V-), U$2.P$3 (A0), U$2.P$4 (GND), U$2.P$7 (GND), U$2.P$8 (REF-), U$2.P$10 (IN-), U$2.P$11 (GND), U$3.P$2 (2), U$6.P$2 (2), U$8.P$3 (GND), U$8.P$4 (/LDAC), U$8.P$5 (/CLR), U$8.P$6 (ADDR), U$9.2 (GND), U$9.3 (SWITCH), U$9.4_1, U$9.4_2, U$10.P$2 (GND), U$11.P$2 (GND), U$12.P$4 (GND), U$13.P$3 (GND), U$15.P$1 (1)
unnamed: U$3.P$1 (1), U$14.COM
unnamed: U$9.1 (CENTER), U$14.3
unnamed: C1.1, C2.1, R8.2, R10.2, U$10.P$1 (IN), U$10.P$3 (EN), U$11.P$1 (IN), U$11.P$3 (EN), U$14.1
unnamed: C3.1, U$10.P$4 (BYP)
unnamed: C4.1, U$11.P$4 (BYP)
unnamed: C6.1, C8.1, C16.1, C17.1, C18.1, C19.1, R6.1, U$1.P$4 (V+), U$2.P$12 (VCC), U$8.P$9 (VDD), U$11.P$6 (OUT), U$12.P$8 (V+), U$13.P$2 (V+)
unnamed: C5.1, C7.1, U1.13 (+3V), U$4.P$1 (1), U$10.P$6 (OUT)
unnamed: C9.1, R3.1, U$1.P$1 (OUTA), U$1.P$2 (-INA)
unnamed: R1.1, U$8.P$1 (VOUT_A)
unnamed: C9.2, R1.2, R2.1
unnamed: U$1.P$8 (OUTC), U$7.P$2 (2), U$12.P$1 (NO1)
unnamed: C10.1, R2.2, U$1.P$3 (+INA)
unnamed: C11.1, U$1.P$6 (-INB), U$1.P$7 (OUTB), U$1.P$10 (+INC)
unnamed: C11.2, R3.2, R4.1
unnamed: C12.1, R4.2, U$1.P$5 (+INB)
unnamed: U$1.P$9 (-INC), U$7.P$1 (1), U$12.P$2 (COM1)
unnamed: U$6.P$1 (1), U$13.P$5 (COM)
unnamed: C13.1, D1.A, D3.C, R5.1, U$1.P$13 (-IND), U$13.P$4 (NC)
unnamed: U$1.P$12 (+IND), U$12.P$5 (NC2), U$13.P$6 (NO)
unnamed: U1.6 (GPIO5), U$12.P$3 (IN2), U$13.P$1 (IN)
unnamed: C13.2, D4.C, D6.A, R5.2, R7.1, U$1.P$14 (OUTD), U$2.P$9 (IN+)
unnamed: D5.A, D6.C
unnamed: D3.A, D5.C
unnamed: D2.C, D4.A
unnamed: D1.C, D2.A
unnamed: U$8.P$2 (VOUT_B), U$12.P$6 (COM2)
unnamed: U1.3 (GPIO2), U$2.P$6 (SDA), U$8.P$8 (SDA)
unnamed: C15.1, U$2.P$1 (REFOUT)
unnamed: C14.1, U$2.P$2 (COMP)
unnamed: R6.2, U$8.P$10 (REF)
unnamed: U1.4 (GPIO3), U$2.P$5 (SCL), U$8.P$7 (SCL)
unnamed: U1.17 (GPIO1), U$5.P$2 (2)
unnamed: U1.16 (GPIO0/AREF), U$5.P$1 (1)
unnamed: U1.14 (RESET), U$4.P$2 (2)
unnamed: U1.5 (GPIO4), U$12.P$7 (IN1)
unnamed: R7.2, R8.1, R9.2, U1.7 (GPIO6), U$15.P$2 (2)
unnamed: LED1.A, R10.1

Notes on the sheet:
Digital
Analog
REF COUNTER
WORKING GND

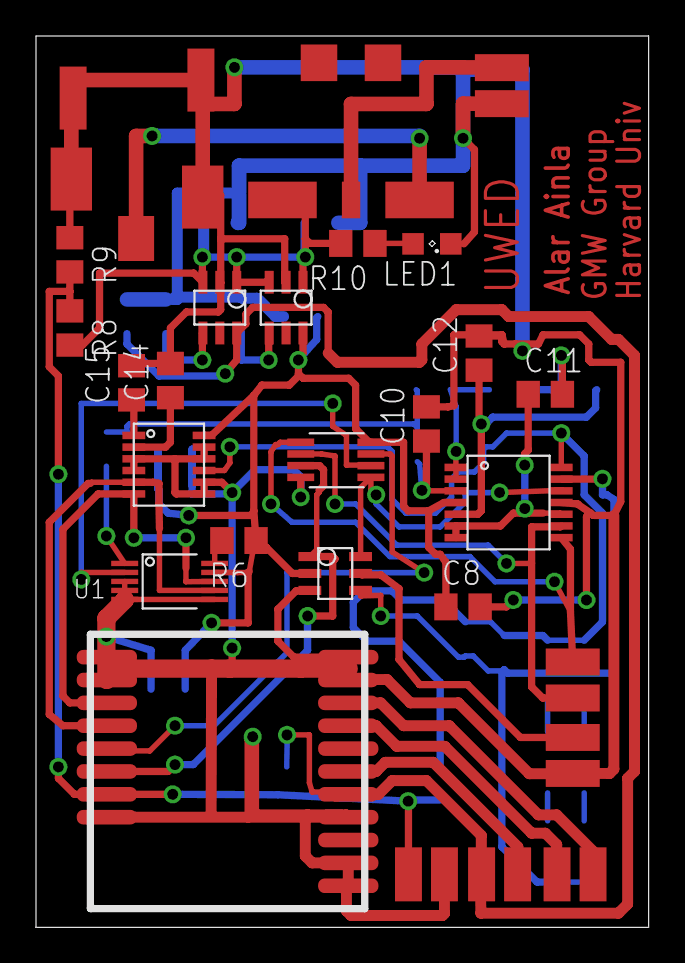
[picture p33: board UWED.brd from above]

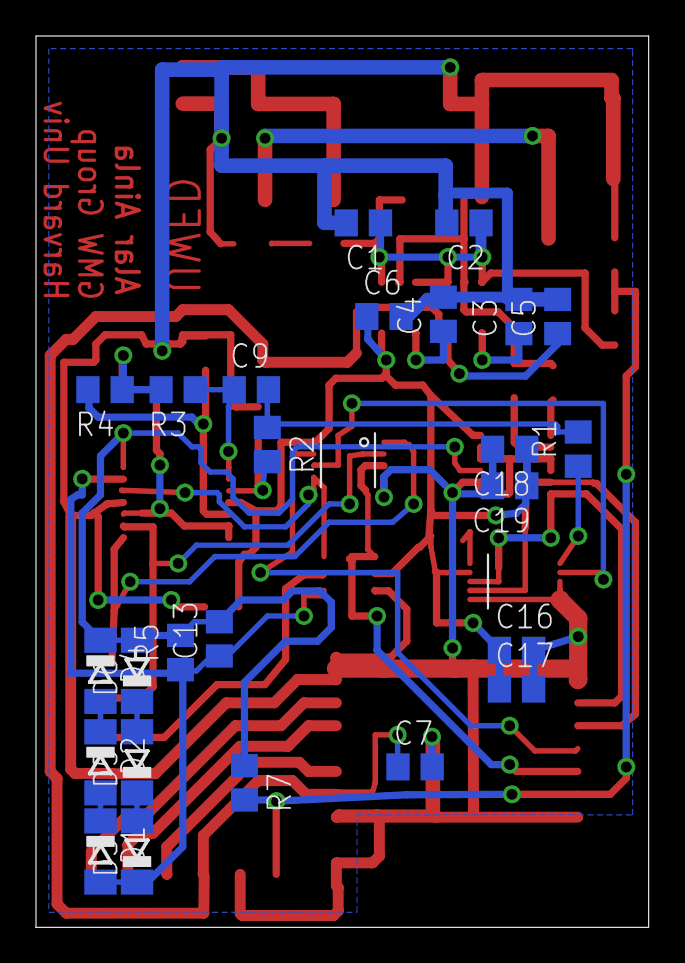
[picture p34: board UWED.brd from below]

Board: 2 copper layers, 34.0 x 49.5 mm, 52 parts (25 on the bottom side), 38 nets.

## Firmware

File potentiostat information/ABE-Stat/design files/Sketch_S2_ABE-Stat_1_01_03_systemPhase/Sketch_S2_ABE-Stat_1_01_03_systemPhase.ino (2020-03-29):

/*
  February 14, 2017 (Started as NC1194_Potentiostat.ino)

  Updated March 23, 2017- largely to address hardware design changes on new design iteration NC1194 Potentiostat V3. These include use of i2c octal switch ADG715 for 
  potentiostat signal switching (A0 and A1 on ADG715 pulled to ground, so i2c address is 0x48). Network analyzer AD5933 address is 0x0D. Other changes are use of 
  low dropout 3.3V regulator AP7365 for wireless devices (high side switching transistor of TPS 62172was not able to deliver required current from single cell Lithium battery),
  corrected i2c pinout for ESP8266 (GPIO5 for SCL, GPIO4 for SDA), and reconfigured potentiostat network (error made in earlier designs).

  Updated dates up to about April 24, 2017- include code to read and communicate temperature, and impedance register values from AD5933 for given frequency, as well as
  current and voltage applied through transimpedance amplifier...

  Updated (to version 04_Exp) on April 30, 2017, for testing various functionality necessary for development of more fully developed Android GUI.

  Changed name to ABE-Stat_1_0_03 (previous versions in summer 2017) on August 20, 2017, mostly to run different basic measurement features of NC1194 Potentiostat. Version 1_0_03 is the
  first to include specific analytical methods (i.e. starting with cyclic voltammetry and electrochemical impedance spectroscopy); ABE-Stat_1_0_04 first version to implement EIS; also polishing
  up CV...

  ABE-Stat 1_0_5 started September 8, 2017- building on fully functional ABE-Stat1_0_04 which has calibration routines including for battery, EIS functions using AD5933 (from 5 kHz to 100 kHz),
  CV functions up to 0.2 scan rate. Adding EIS functionality from 0.1Hz to about 100 Hz using signals generated entirely from DAC5061, and DFT of TIA samples from ADS1220 (in this case running 
  in turbo mode at highest data rate 2000 sps...

  ABE-Stat 1_0_06 started September 14, 2017; admittance vs frequency calibrations change with different AD5933 settings (i.e. PGAx5GainSetting, excitationCode, and TIAGainCode;
  so update calibration routines to calibrate admittance magnitude (scaled by load resistor from calibration
  Version 06_worked on through September 26 2017 to include open circuit configuration and open circuit voltage measurement (i.e. pH electrode); upgraded this version through
  September 26 to include calibration for every setting of AD5933, and all basic interfaces with Android ABE-Stat app through Cyclic Voltammetry and Electrochemical
  Impedance spectroscopy, including for low frequencies using ADC (ADS1220) for customized single frequency DFT...

  ABE-Stat_1_0_07 started September 27, 2017; simple check for TIA saturation not always effective (at saturation amplifier inputs violate ideality(?) and the observed TIA output voltage 
  is not always close to positive analog rail value (i.e. in some instances is lower than 1 V)- so updated resistance measurement, current measurements, and EIS measurements
  to confirm linearity of a result at a different setting before accepting a value... Also, added methods to conduct Differential Pulse Voltammetry.
  Also included a firmware number to report back to Android... Also tried to check all calculated values for divide by 0 to prevent "nan" or "inf" being written to Android when it expects
  a parsable number string...

  ABE-Stat_1_0_08 October 26; add code to shut off power after 1 minute idle with no bluetooth connection.
  ABE-Stat_1_0_09 November 3, 2017; blink LED a few times and turn off if battery is discharged; corrected EEPROM_Int_Write so that 16 bit value gets written to two 8 bit blocks (previously LSB overwrites MSB)

  ABE-Stat_1_0_10 December 15, 2017, turn off WiFi at startup, and keep off to suppress noise; also increase update rates for CV to try to smooth applied potential

  ABE-Stat_1_01_00 started January 19, 2018, update functions to use external clock 250kHz clock with AD5933 for lower frequency EIS; update requires updated board design ABE-Stat_1.0.01
  (previous versions worked with NC-1194_Potentiostat). Need to add additional EEPROM and calibration assignments to calibrate device operating over new frequencies and clock,
  and ABE-Stat_DigitalConfigurations (i.e. !O12 controls power enable to AD5933 and external clock- leave off for other voltammetric applications to limit noise).
  Also update DigitalConfigurations to use ADG715 S02 to make biasing amplifier a voltage follower for open circuit configuration (don't allow unpredictable leakage from drifting
  output). (used for preliminary testing of EIS with MCLK external clock, and also some troubleshooting to improve LED modulation for indicating charge state)

  ABE-Stat_1_0_01 finished preliminary function updates to enable rough characterization of AD5933 with slower clock (changed frequency argument to double data type,
  fixed bug where device gets stuck in infinite loop in TestImpedance(), and also checked for repeating admittance magnitudes (sign that AD5933 no longer reading commands correctly;
  situation is addressed by cycling power to AD5933 and repeating measurement.
  
  ABE-Stat_1_01_02 started March 13, 2018, used to test EIS characteristics for different passive component networks (mostly update EIS Analysis for new 

  ABE-Stat_1_01_02_700HzTest March 14, to compare AD5933 Vout / synthesizer signal to signal applied at reference pin to determine source of signal distortions near 700 Hz...
  To facilitate oscilloscope measurement, long delays are embedded in TestImpedance function to ensure signals are generated for long periods of time...

  ABE-Stat_1_01_03_500HzTest started May 9, 2018; to work with hardware version ABE-Stat 1_0_02, (separate power controller on O13 for AD5933 external clock); calibration
  indicates ~500Hz harmonic distortion in signal...
  
  Shift register outputs (2x serialized 74HC595, O00 - O15):
      O00 74LVG1G53 switch1 signal (!CS to !CS1 (ADS1220/ "0") or !CS2 (AD5061/ "1")
      O01 74LVG1G53 switch1 !enable (!CS1 && !CS2 pulled high if O01 high)
      O02 74LVG1G53 switch2 signal (RN42 BT_Connected "0" or ADS1220 !DRDY "1" to GPIO00)
      O03 74LVG1G53 switch2 !enable (GPIO00 floats when O03 high)
      O04 ADG779 switch1 signal (TIA feedback to LMP7721 Vout "0" or AD59933 RFB "1")
      O05 ADG779 switch2 signal (TIA input to LMP7721 V- "0" or AD5933 Vin "1")
      O06 Input to illuminate red segment of 3-color LED
      O07 PMOS gate driver for multicolor LED (active low)
      O08 / O09 A0 and A1 of ADG704 switch (set TIA gain, 00 = 100M; 01 = 10k; 10 = 1M; 11 = 100
      O10 TIA gain setting enable (otherwise feedback is open circuit)
      O11 Software shutoff ("0" removes power from circuit, but only when no USB supply is provided)
      O12 !Enable for AD5933 and external clock power (leave off / high for voltammetric applications to remove potential source of noise

      O12 - O15 general purpose outputs broken out to board periphery (careful using O12 as on ABE-Stat hardware implementation; can 
        conflict with enable / power circuit for AD5933

  ADG715 Switch Connections (S0 - S7; states set by state of corresponding bit written to i2c address 0x48):
      S0 Connect working electrode to TIA
      S1 Not used (contacts held at ground)
      S2 voltage follower on biasing amplifier (use to stabilize output in open circuit configuration)
      S3 Feedback reference electrode to amplifier setting counter electrode potential
      S4 Connect Counter electrode amplifier output to reference electrode (connect counter and reference electrodes)
      S5 Connect counter electrode to it's amplifier output
      S6 Sum AD5933 output/ signal source into potentiostat network
      S7 Sum AD5061 DAC voltage into potentiostat network
   
by Daniel M. Jenkins
*/

#include <SPI.h>
#include <Wire.h> // reserved for when we start communicating with AD5933
#include <EEPROM.h>

#include "ESP8266WiFi.h"  // necessary for disabling WiFi- try to suppress extra noise

// IO for SPI communication  (CS shared with shift register clock )
#define MISO             12
#define MOSI             13
#define SCK              14
#define CS_RCK           15 // shared with shift register clock

//inputs to shift register (configure as outputs from ESP8266)
#define SER              16 // data into shift registers
#define CLOCK            2  // clock data in from SER to data registers (note that this is separate from the register clock)

// i2c and SPI default pins based on definitions using the pinout shown at https://github.com/esp8266/Arduino/blob/master/doc/reference.md 

// GPIO00 assigned as input (listen for either !DRDY from ADS1220, or BluetoothConnected Signal)
#define GPIO00            0

// map to connect ESP8266 !CS to corresponding !CS pins on ADS1220 or AD5061 (only allow one to connect at a time, other is always pulled high- make sure that both
// devices are not writing to MISO simultaneously (even though AD5061 doesn't have a data out pin)
#define ADS1220_ADC          0  // SPI chip select designation for ADS1220 (value on shift register output 00 to connect !CS to ADS1220)
#define AD5061_DAC           1  // SPI chip select designation for AD5061 (value on shift register output 00 to connect !CS to AD5061)

#define BAUD             115200 // baud rate for serial communication

// i2c addresses
#define ADG715OctalSwitch      0x48
#define AD5933NetworkAnalyzer  0x0D

// Control / data register assignments for network analyzer
#define AD5933_Control            0x80  // 2 byte control register
#define AD5933_StartFrequency     0x82  // 3 byte control register
#define AD5933_FrequencyIncr      0x85  // 3 byte control register
#define AD5933_IncrNumber         0x88  // 2 byte control register
#define AD5933_SettleCycleNumber  0x8A // 2 byte control register
#define AD5933_Status             0x8F   // 1 byte status register
#define AD5933_TemperatureData    0x92  // 2 byte data register
#define AD5933_RealData           0x94  // 2 byte data register
#define AD5933_ImaginaryData      0x96  // 2 byte data register


// Addresses in EEPROM for calibration constants/ coefficients
const int EEPROMBlockSize = sizeof(double); // so maximum double precision values to store in EEPROM is 512 (4096 / 8)

#define DAC_SLOPE_EEPROM_ADDRESS      0
#define DAC_OFFSET_EEPROM_ADDRESS     EEPROMBlockSize
#define DAC_LOW_LIMIT_EEPROM_ADDRESS   2 * EEPROMBlockSize
#define DAC_HIGH_LIMIT_EEPROM_ADDRESS  3 * EEPROMBlockSize

#define GAIN_0_EEPROM_ADDRESS         4 * EEPROMBlockSize
#define GAIN_1_EEPROM_ADDRESS         5 * EEPROMBlockSize
#define GAIN_2_EEPROM_ADDRESS         6 * EEPROMBlockSize
#define GAIN_3_EEPROM_ADDRESS         7 * EEPROMBlockSize

#define PHASE_SLOPE_EEPROM_ADDRESS    8 * EEPROMBlockSize // these are now the base addresses for these values- now that we have different calibration data for each of 24 settings on AD5933
#define PHASE_OFFSET_EEPROM_ADDRESS   9 * EEPROMBlockSize
#define Z_SLOPE_EEPROM_ADDRESS        10 * EEPROMBlockSize
#define Z_OFFSET_EEPROM_ADDRESS       11 * EEPROMBlockSize

  // after inclusion of calibration with external clock, memory start address for G_PER_V is 200 = (48 * 4) blocks of double values for 48 different settings, + 8 double values for DAC and TIA Gain calibration values
#define AD5933_G_PER_V_EEPROM_ADDRESS 200 * EEPROMBlockSize // prior to calibrations for external clock, starting block address 104 = (24 * 4) blocks of double values for impedance / phase calibration coefficients for 24 different settings, + 8 double values for DAC and TIA Gain calibration values
#define AD5933_BIAS_uV_EEPROM_ADDRESS 201 * EEPROMBlockSize

#define V_BATT_FULL_EEPROM_ADDRESS    202 * EEPROMBlockSize  // note that this is simply a 16 bit number- 10 bit value summed 64 times (saved as 16 bit unsigned integer in a 2 byte block)
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

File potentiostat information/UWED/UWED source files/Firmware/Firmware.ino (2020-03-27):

// -------------------------------------------------------------------------
// This is a firmware code for UWED
// Hardware platform rfDUINO
// Other components are two channel 16-bit DAC and one channel built in 10-bit ADC
// Developed by Alar Ainla, 2016-2018. Whitesides Group. Harvard University
// Commands are sent in ASCII text format, data is sent in binary format.
// -------------------------------------------------------------------------

//Include RFDUINO definitions
#include <RFduinoBLE.h>
//Use Wire library for I2C communications
#include <Wire.h>

//---------------------------------------------------------------
// --- DEVICE CONFIGURATIONS
//---------------------------------------------------------------
//I2C Pins
#define SDApin 2
#define SCLpin 3
//Switch 1: voltage vs current measurement (0-> Current, 1->Voltage). Digital output
#define SwitchIV 5
//Switch 2: reference electrode (0->3 electrode, 1->2 electrode). Digital output
#define SwitchEl 4
//Analog signal input pin
#define ADCIn 6

//--- BLE parameters ---
//Device BLE name
#define DEVICE_NAME "UWED"

//--- Other hardware definitions ---
//DAC reference electrode channel
#define DAC_RefCH 0
//DAC working electrode channel
#define DAC_WCH 1

//---------------------------------------------------------------
// --- ALL VARIABLES AND SETTINGS
//---------------------------------------------------------------

//--- System setting ---
volatile unsigned int refPot=0;             //Reference electrode potential DAC value
volatile unsigned int wPot=0;               //Working electrode potential DAC value
char inpMode=0;                             //Input mode 0-potentiometric, 1-amperometric
char nrEl=3;                                //Number of electrodes. 2 or 3
volatile uint_fast16_t timerBaseStep = 25;  //This is timer base step in ms (for interupts). Tested frequencies value --> Measured: 15 --> 67.5Hz, 10 --> 100Hz, 25 -->40.42Hz
volatile uint_fast16_t timerBaseStep1 = 25; //This is timer base step 1 (odd): this value is used for all measurements but DPV, in which case both timerBaseStep1 and 2 are used.
volatile uint_fast16_t timerBaseStep2 = 0;  //This is timer base step 2 (even): which is used only for DPV. In all other cases it should be 0 and only value "1" is used. Default
int refIncOdd=0;    //Reference channel increment at odd steps
int refIncEven=0;   //Reference channel increase at even steps
int wIncOdd=0;      //Working channel increase at odd steps
int wIncEven=0;     //Working channel increase at even steps
int numberOfSteps=0;   //Number of steps to make
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

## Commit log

2020-03-25 Update and rename readme.md to pcbNotes
2020-03-25 Update and rename pcbNotes to pcbNotes.md

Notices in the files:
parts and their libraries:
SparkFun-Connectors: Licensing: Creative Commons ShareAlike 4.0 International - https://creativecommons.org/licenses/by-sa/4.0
